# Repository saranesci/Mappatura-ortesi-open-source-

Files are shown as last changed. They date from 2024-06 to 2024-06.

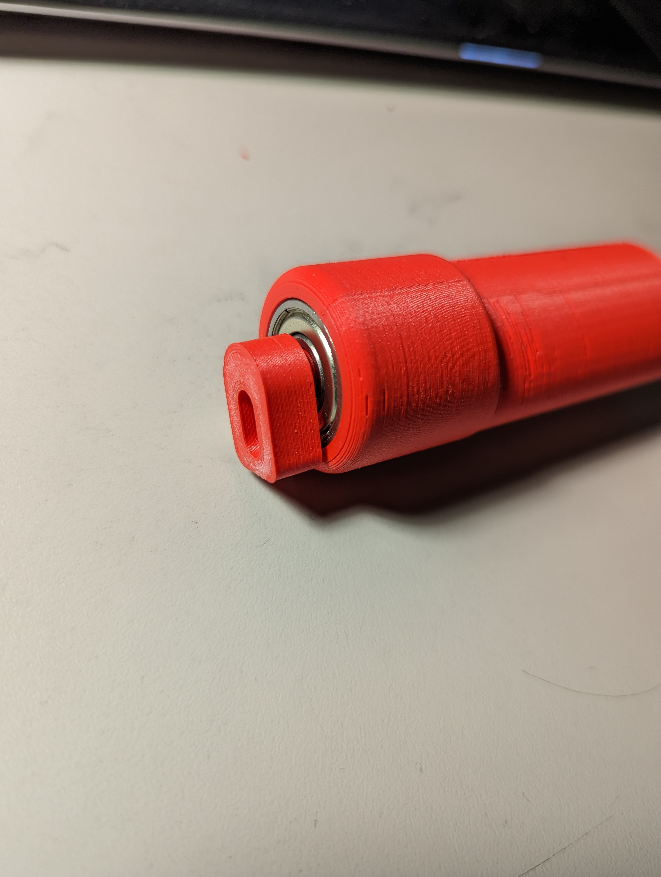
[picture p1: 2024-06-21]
Spoon stabilizer support/spoon-stabilizer-support-main/Photos/handle assembly.jpg

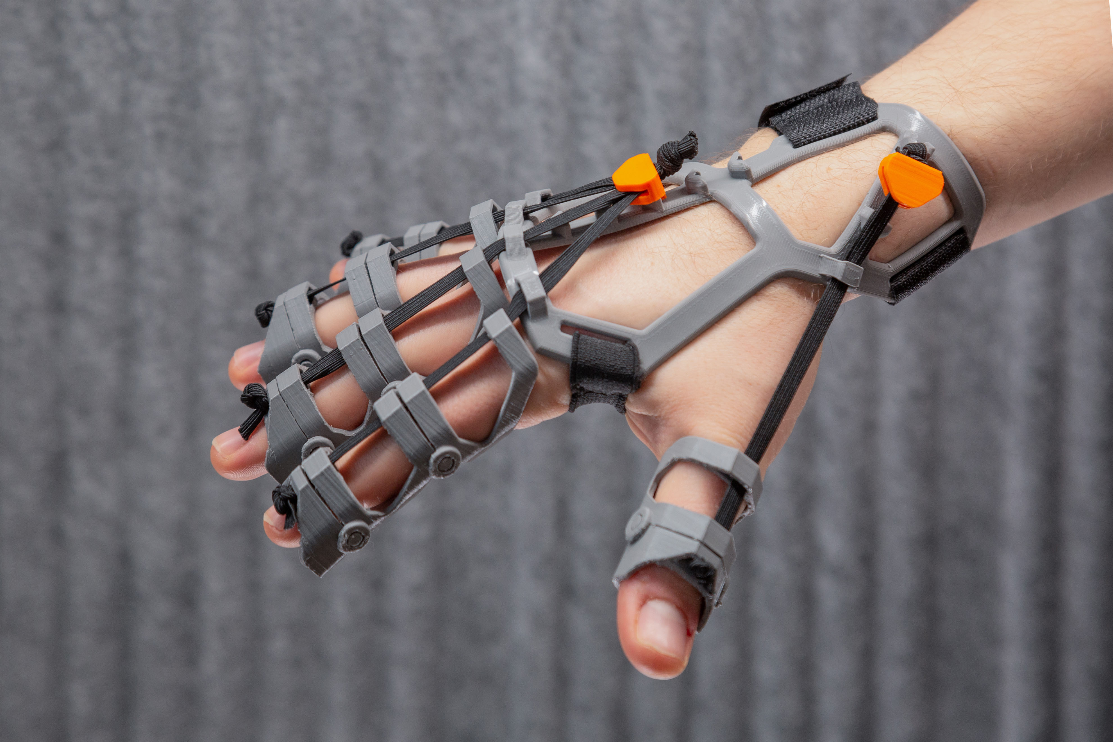
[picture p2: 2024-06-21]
Improving fine motor skills, designing a 3D FDM printed orthosis to assist in the rehabilitation of individuals with hand spasticity/images/9a8a8b08-8b19-4f01-8956-d06154abd471.jpg

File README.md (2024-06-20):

# Mappatura-ortesi-open-source-
Questo repository è una raccolta di soluzioni open source progettate per supportare i lavoratori con disabilità e aiutarli a svolgere le loro mansioni in modo sicuro ed efficiente. L'obiettivo è promuovere l'inclusione lavorativa fornendo un accesso gratuito e aperto a soluzioni assistive innovative.

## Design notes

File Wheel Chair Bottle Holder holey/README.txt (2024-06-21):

Wheel Chair Bottle Holder holey by Diselico on Thingiverse: https://www.thingiverse.com/thing:3944166

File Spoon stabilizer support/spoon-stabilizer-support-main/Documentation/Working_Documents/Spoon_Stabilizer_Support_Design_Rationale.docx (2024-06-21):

# Introduction

A device for those who have difficulties with tremors when eating. It used both passive stabilization and weights to dampen the effect of hand tremors.

# Research

Below is a table of existing commercial or DIY options that are similar.

Name | Picture | Price | Link

Commercial

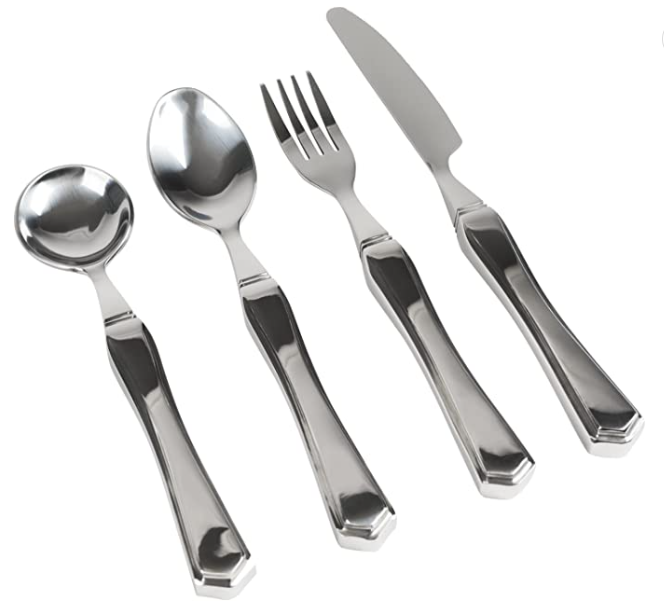
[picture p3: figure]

Vive Weighted Utensils | | $55.46 | Link (https://www.amazon.ca/Vive-7oz-Weighted-Utensils-Piece/dp/B075Y3N1MZ)

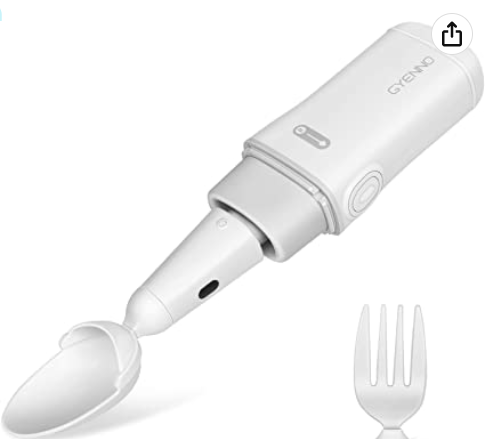
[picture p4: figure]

GYENNO Bravo Twist | | $399 | Link (https://www.amazon.ca/GYENNO-Twist-Parkinson-Stabilizing-Parkinsons/dp/B07FRPX2H8?hvadid=353068188462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)

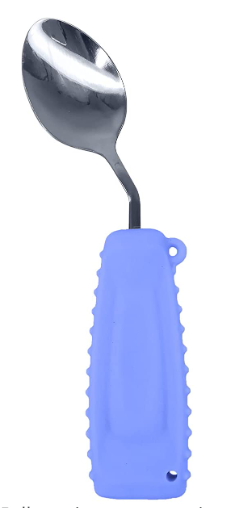
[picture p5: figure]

Ehucon Adaptive Utensils | | $22.32 | Link (https://www.amazon.ca/Ehucon-Untensils-Parkinsons-Lightweight-Ergonomic/dp/B09QGBSPK9?hvadid=353068188462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)

DIY

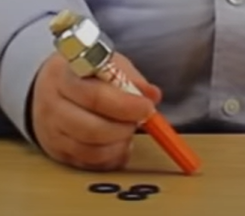
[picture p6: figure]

DIY Weighted Marker | | N/A | Link (https://www.youtube.com/watch?v=PVcX0uTqMMg)

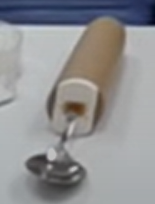
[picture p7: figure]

DIY Weighted Fork | | N/A | Link (https://ohanaot.com/make-weighted-pencil-fork-spoon-kids-autism/)

# Requirements

## Goals

G01 | Create a weighted utensil that stabilizes the tremors of a user’s hand

## Functional Requirements

F01 | Device must be weighted
F02 | Device must have passive spill prevention
F03 | Device must be cleanable

## Non-functional Requirement

NF01 | Device must be made from off the shelf components and 3D printed parts

## Constraints

C01 | Device must cost less than 10 dollars

# Testing

After assembling the device, it was tested to see if it would fail. It was found that 20% infill was too weak for some parts, so they were changed to 100% infill for added strength.

# Opportunities for Improvement

The device could be printed in ABS or another dishwasher safe material.

Printability improvements could be made to reduce support use.

© 2023 by Neil Squire. This work is licensed under the CC BY SA 4.0 License: http://creativecommons.org/licenses/by-sa/4.0 Files available at https://makersmakingchange.com/project/spoon-stabilizer-support/ Page 2 of 3

V1.0 | February 2023 Spoon Stabilizer Support Design Rationale

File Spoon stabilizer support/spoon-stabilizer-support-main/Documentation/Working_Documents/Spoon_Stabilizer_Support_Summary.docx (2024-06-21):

# Title

Spoon Stabilizer Support

## Subtitle

A device for those who have difficulties with tremors when eating. The Spoon Stabilizer Support uses both passive stabilization and weights to dampen the effect of hand tremors.

## Device Details

### Overview

A device for those who have difficulties with tremors when eating. It used both passive stabilization and weights to dampen the effect of hand tremors.

### Usage

Attach either the spoon or fork attachment to the handle using the set screw. The device can then be used as a normal spoon or fork.

### Cost

<$5

### Build Instructions

After all supports are removed, superglue the bearing into the handle, and the insert into the bearing. Cut the spoon near the head, and glue it into the spoon attachment. Connect the spoon attachment to the insert using the computer case screws. If the user wants a weighted handle, insert the fishing weights into the handle. Finally, glue the grip insert onto the end of the handle.

#### Skills Required

- 3D Printing

#### Time Required

3D Printing Time: 308 min

Assembly Time: 10 min

#### Tools

- 3D Printer
- Tin Snips
- Superglue
- Hot Glue

#### Components

- Bearings
- Computer Case Screws
- Fishing Weights
- Utensil

#### 3D Printing

- Grip Handle
- Grip Insert
- Insert
- Spoon attachment

### Attribution

Design by Ian Faulkner (https://www.printables.com/social/380579-ian-faulkner/about)

Documentation by Neil Squire Society/Makers Making Change

© 2023 by Neil Squire. This work is licensed under the CC BY SA 4.0 License: http://creativecommons.org/licenses/by-sa/4.0 Files available at https://makersmakingchange.com/project/spoon-stabilizer-support/ Page 2 of 3

V1.0 | February 2023 Spoon Stabilizer Support Summary

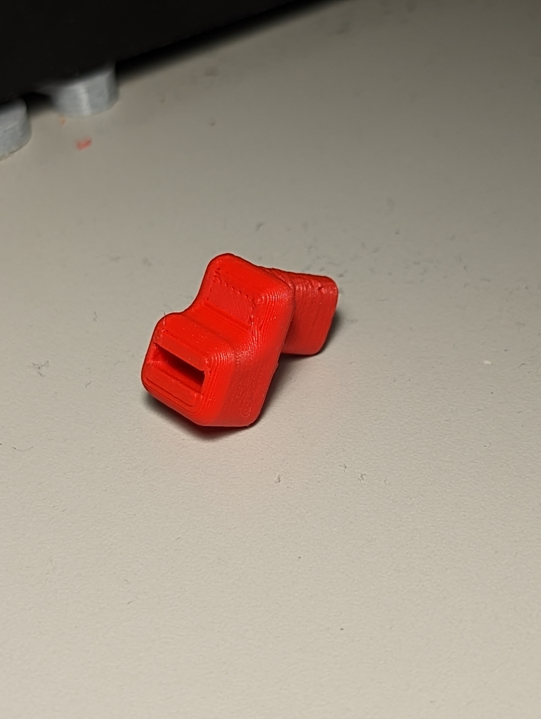
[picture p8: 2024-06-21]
Spoon stabilizer support/spoon-stabilizer-support-main/Photos/spoon attachment.jpg

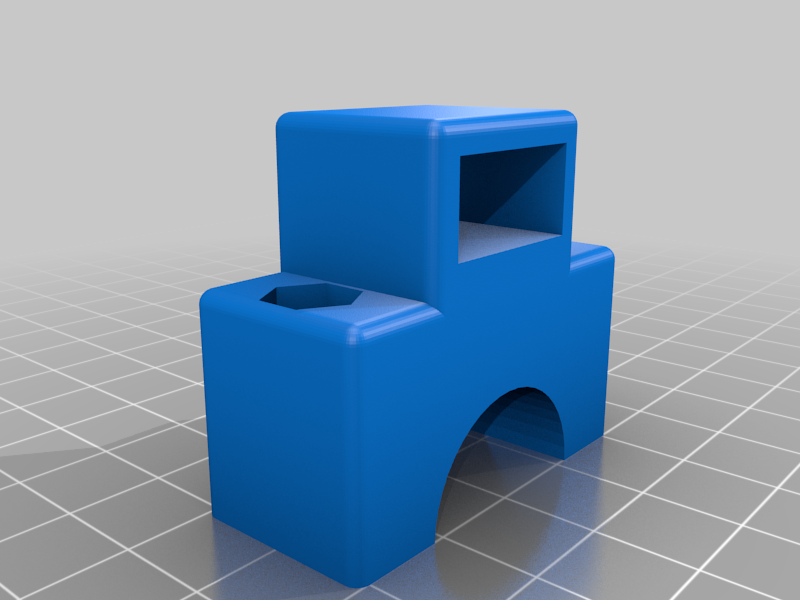
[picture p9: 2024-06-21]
Wheel Chair Bottle Holder holey/images/4a7bebc6-be08-4650-9d3e-f749b71c4481.png

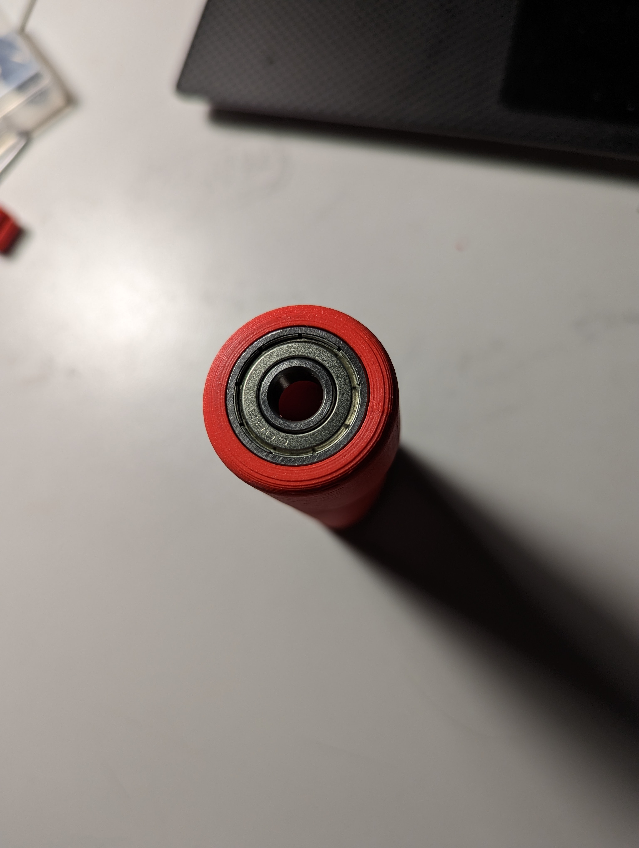
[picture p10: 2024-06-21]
Spoon stabilizer support/spoon-stabilizer-support-main/Photos/bearing inserted.jpg

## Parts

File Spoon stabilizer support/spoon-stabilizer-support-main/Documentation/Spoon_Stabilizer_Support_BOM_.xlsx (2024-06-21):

Device: Spoon Stabilizer Support |  | Total Cost | Total Print time (hr) | Total filament (g)
Version: V1.0 | Date Created: 2/14/2023 | $6.95 | 4.97 | 33
Commercial Parts:
Part type (Electrical. Mechanical, Sanitization, ect) | Part Name | Quantity Needed | Pkg Quantity | Price per package | Price per Unit | Price for qty needed | Link
Mechanical | Bearings | 1 | 10 | $11.55 | $1.16 | $1.16 | https://www.amazon.ca/gp/product/B07XLV1W2M/ref=ppx_yo_dt_b_asin_title_o00_s00?ie=UTF8&psc=1
Mechanical | Computer Case Screws | 1 | 10 | $9.89 | $0.99 | $0.99 | https://www.amazon.ca/gp/product/B07TXS98L6/ref=ppx_yo_dt_b_asin_title_o00_s00?ie=UTF8&psc=1
Mechanical | Fishing Weights | 2 | 10 | $13.99 | $1.40 | $2.80 | https://www.amazon.ca/gp/product/B0B1JBJ91F/ref=ppx_yo_dt_b_asin_title_o00_s00?ie=UTF8&psc=1
Mechanical | Spoon | 1 | 12 | $14.17 | $1.18 | $1.18 | https://www.amazon.ca/Winco-0005-03-12-Piece-Dinner-Stainless/dp/B004UNF2II
3D Printed Parts ESTIMATED PRICING USING 1KG ROLL COST: | $25.00
Part | Description | Quantity Needed | TOTAL Mass (g) | Estimated Price | Print Time (Min) | Link
Grip Handle | Main Handle | 1 | 26 | $0.65 | 224
Grip Insert | Handle endcap | 1 | 2 | $0.05 | 15
insert | Connects spoon to bearing | 1 | 2 | $0.05 | 27
spoon attachment | Connects to spoon | 1 | 3 | $0.07 | 32
 |  |  |  | $0.00
 |  |  | Total Print Cost: | $0.83
Tools for Assembly
Alternatives (if there are other sources for some parts link them below)
Part and description | Link

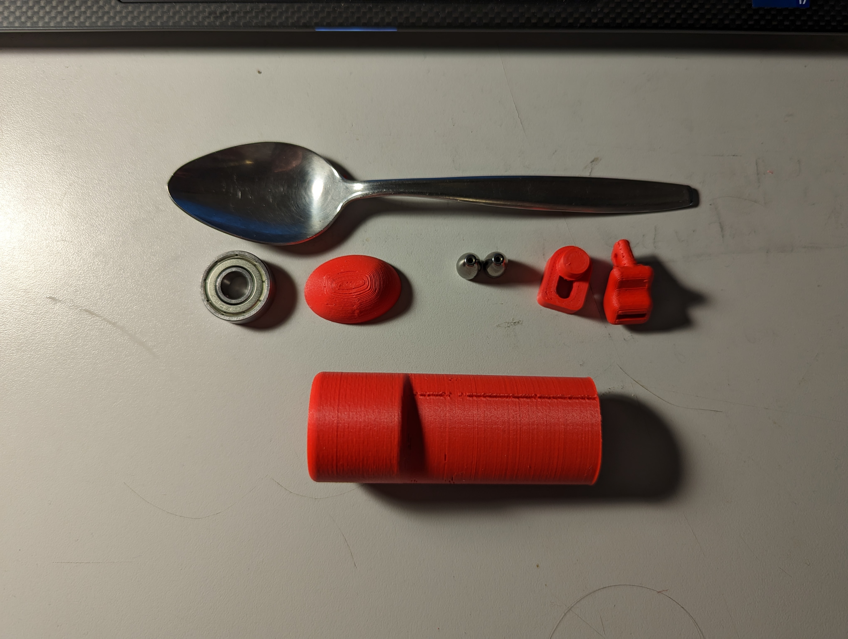
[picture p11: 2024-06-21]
Spoon stabilizer support/spoon-stabilizer-support-main/Photos/Parts layout.jpg

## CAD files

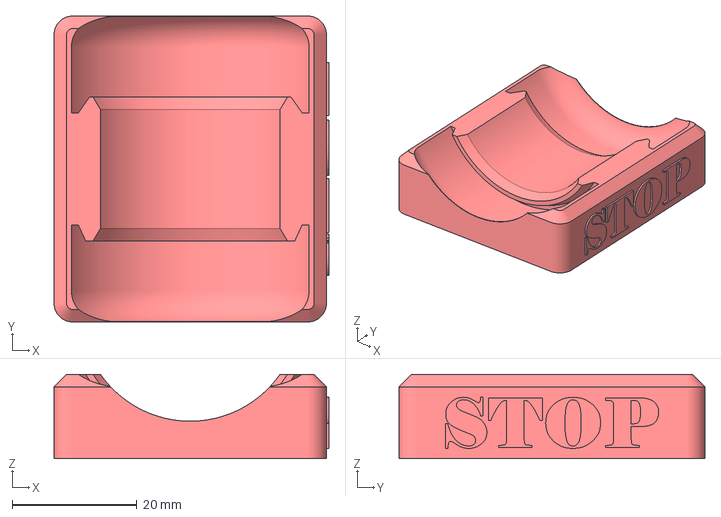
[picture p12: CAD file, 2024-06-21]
Chair stop wheel holder/Chair Stop, Wheel holder.3mf
44.0 x 49.0 x 13.5 mm

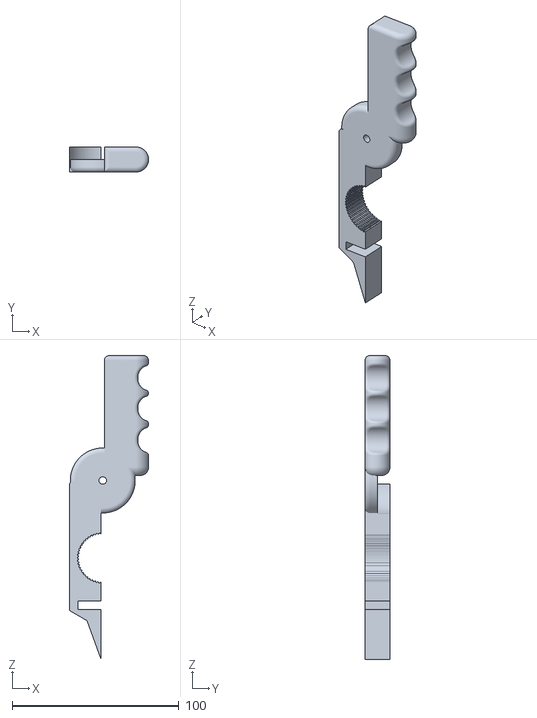
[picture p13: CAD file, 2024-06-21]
Gripsy - Tool for disabled people/files/gripsy_left.stl
47.5 x 15.0 x 182.4

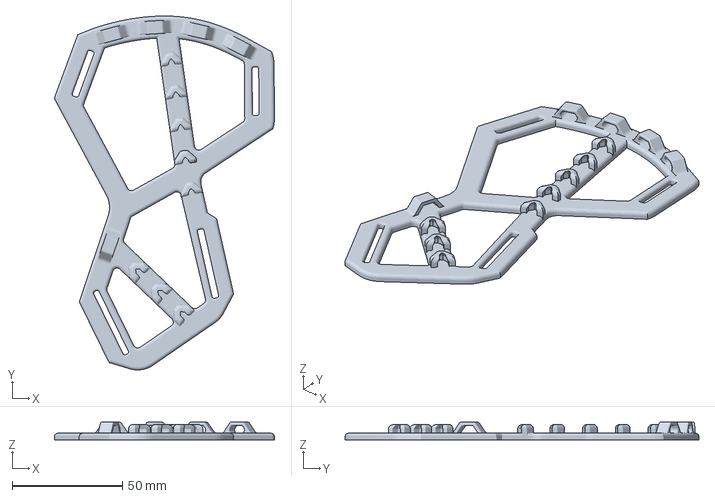
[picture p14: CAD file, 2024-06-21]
Improving fine motor skills, designing a 3D FDM printed orthosis to assist in the rehabilitation of individuals with hand spasticity/files/hand_heated_part.3mf
99.8 x 160.6 x 8.00 mm

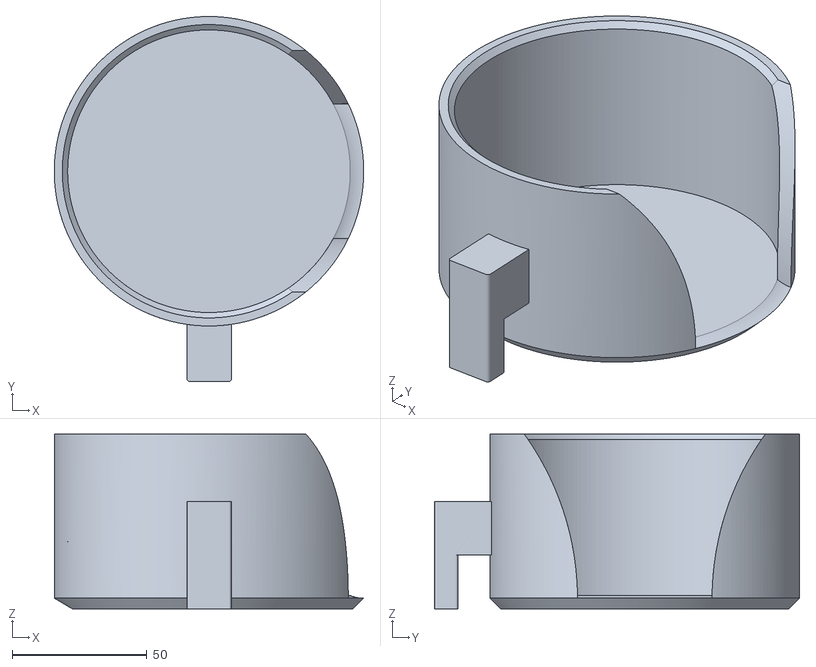
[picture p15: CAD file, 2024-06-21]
NewSkill wheelchair cup holder/files/cup_right.stl
115.0 x 135.6 x 65.0

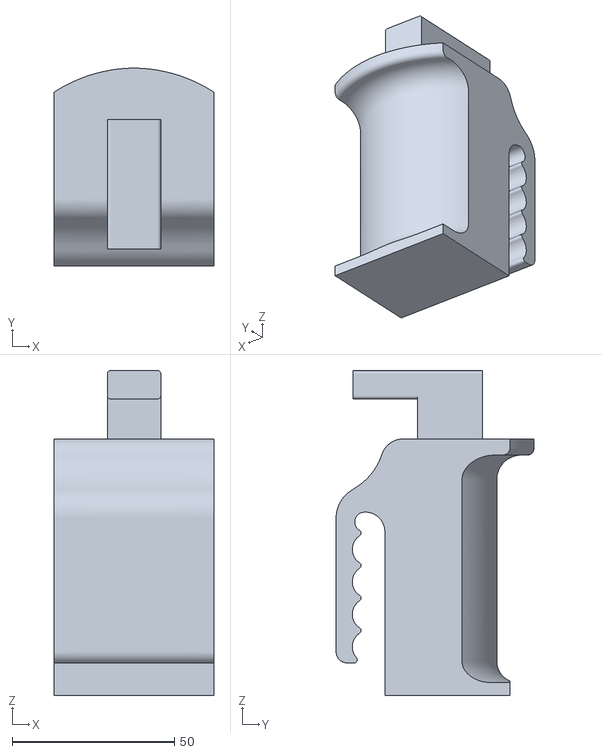
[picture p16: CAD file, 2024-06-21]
NewSkill wheelchair cup holder/NewSkill wheelchair headphones holder - 6606261/files/Headphones_Holder.stl
49.2 x 60.9 x 100.1

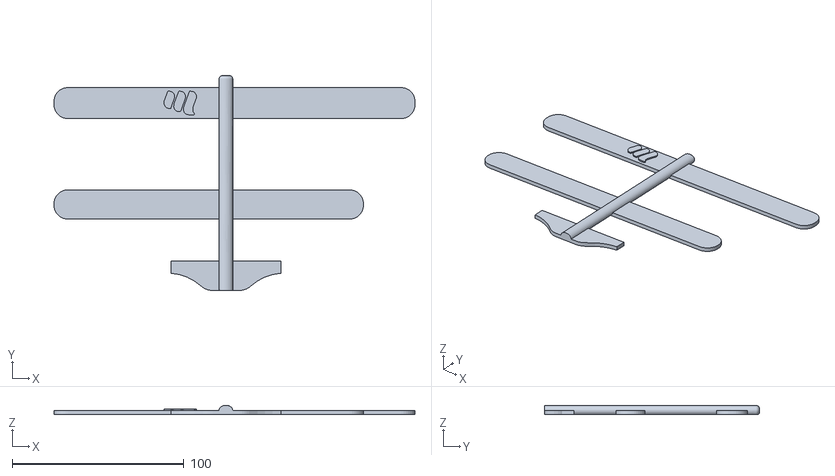
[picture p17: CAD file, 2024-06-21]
Orthosis for Typing and touchscreen/files/Typing_orthosis.STL
210.0 x 125.0 x 5.50

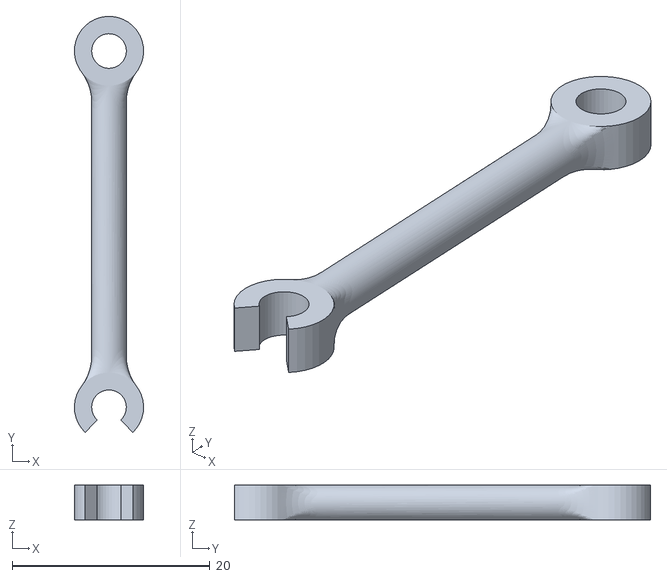
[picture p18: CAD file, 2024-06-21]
Printed Rehabilitation Orthosis/3D Printed Orthosis Free Source Files and Assembly Guide/Finger 1/1d.STL
7.00 x 42.0 x 3.50

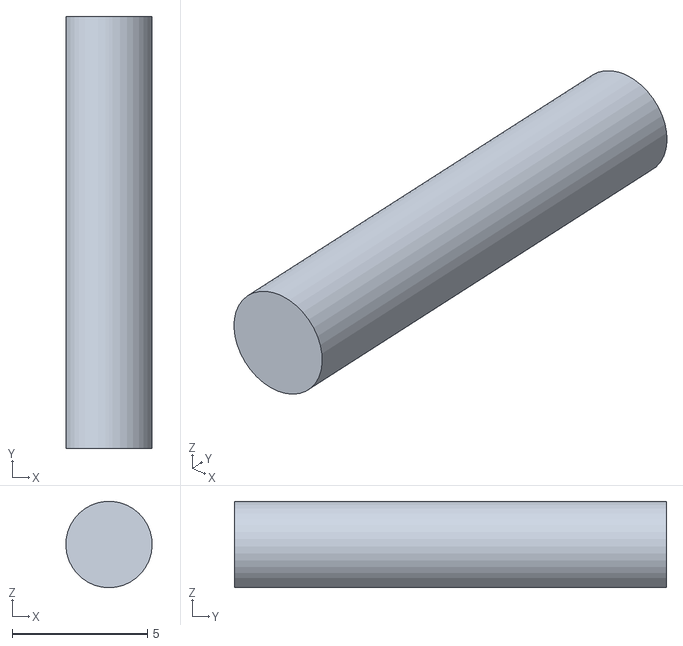
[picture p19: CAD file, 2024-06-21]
Printed Rehabilitation Orthosis/3D Printed Orthosis Free Source Files and Assembly Guide/Finger 2/2k.STL
3.20 x 16.0 x 3.20

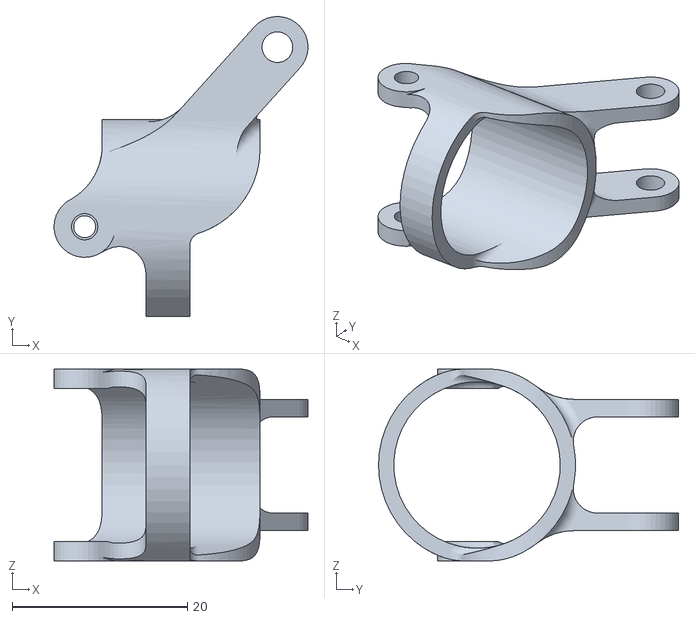
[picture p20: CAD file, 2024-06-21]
Printed Rehabilitation Orthosis/3D Printed Orthosis Free Source Files and Assembly Guide/Finger 3/3c.STL
29.0 x 34.2 x 21.9

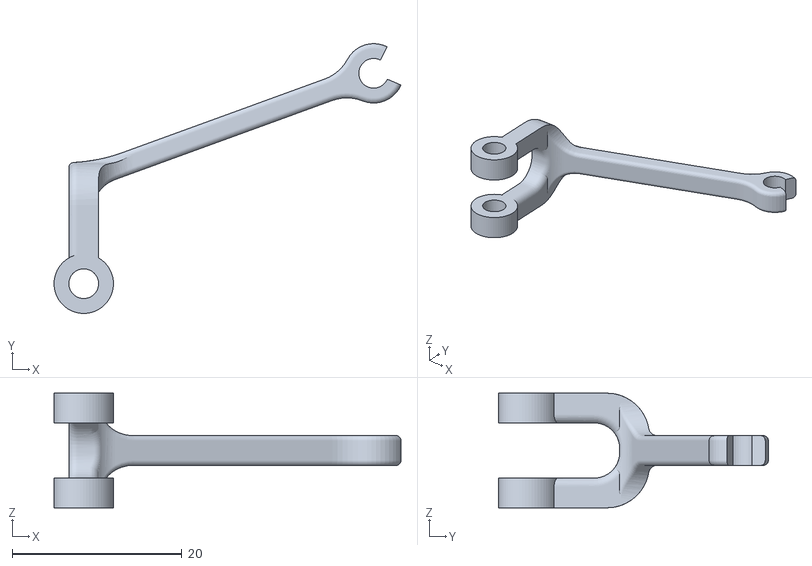
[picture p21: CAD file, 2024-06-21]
Printed Rehabilitation Orthosis/3D Printed Orthosis Free Source Files and Assembly Guide/Finger 4/4f.STL
40.8 x 31.8 x 13.5

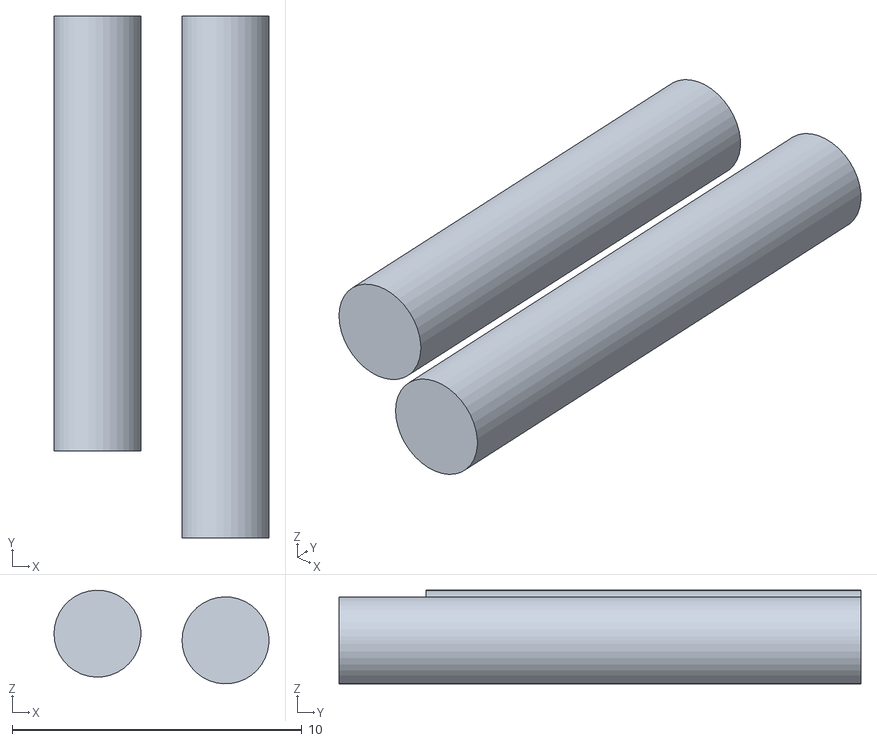
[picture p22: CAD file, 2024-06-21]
Printed Rehabilitation Orthosis/3D Printed Orthosis Free Source Files and Assembly Guide/Finger 5/5h.STL
7.42 x 18.0 x 3.23

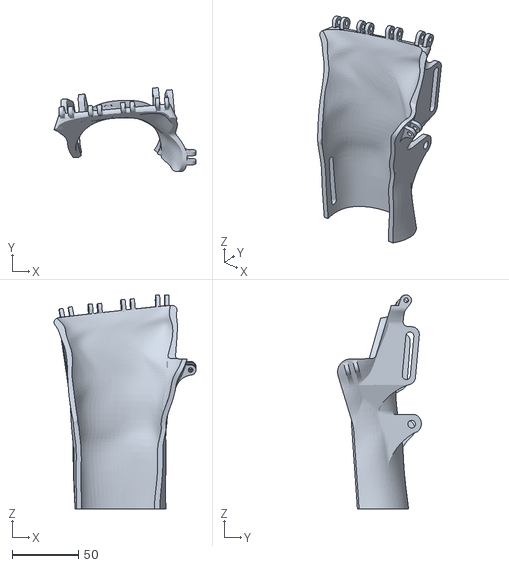
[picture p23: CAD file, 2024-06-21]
Printed Rehabilitation Orthosis/3D Printed Orthosis Free Source Files and Assembly Guide/Husk/0.STL
107.1 x 63.3 x 161.5

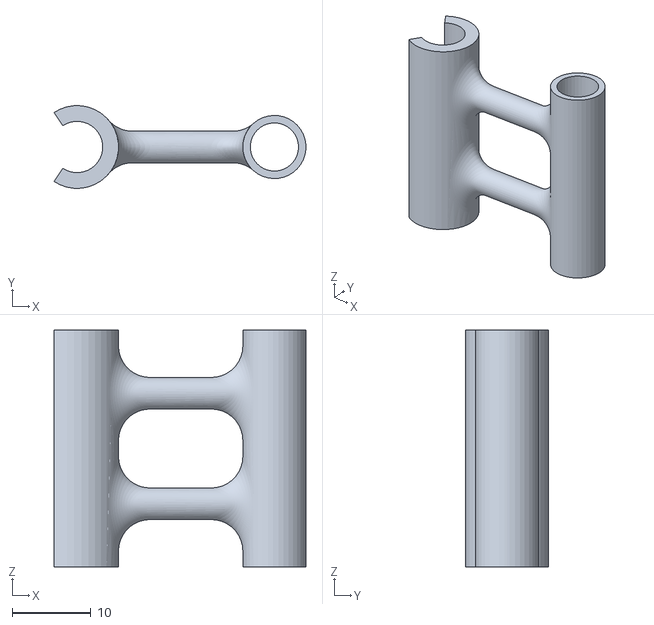
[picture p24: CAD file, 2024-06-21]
Printed Rehabilitation Orthosis/3D Printed Orthosis Free Source Files and Assembly Guide/Lever mechanism and pin/6c.STL
31.9 x 10.5 x 30.0

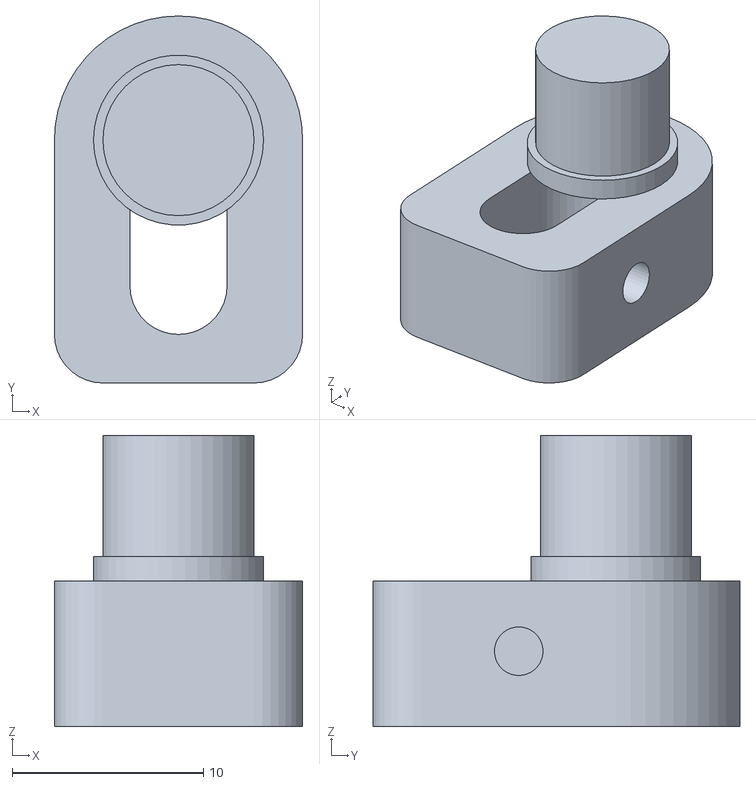
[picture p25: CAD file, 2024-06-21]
Spoon stabilizer support/spoon-stabilizer-support-main/Build_Files/3D_Printing_Files/insert.STL
13.0 x 19.2 x 15.2

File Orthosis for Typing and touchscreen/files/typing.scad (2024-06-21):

/* [Parameters] */
tip_perimeter=64;
tip_width=17;

mid_perimeter=200;
mid_width=17;

bottom_perimeter=210;
bottom_width=17;

distance_tip_mid=24.5;
distance_mid_bottom=41.5;

thickness=2.5;

/* [Hidden] */
e=thickness;
r=8;
r2=2;
tfp=tip_perimeter;
tfw=tip_width;

mp=mid_perimeter;
mw=mid_width;

bp=bottom_perimeter;
bw=bottom_width;

dtm=distance_tip_mid;
dmb=distance_mid_bottom;

//modulos
module cubox(l1,w1,e1,r1){
hull(){
translate([l1/2-r1,w1/2-r1,0]){
cylinder(e1,r1,r1,$fn=100, center=true);
}
translate([l1/2-r1,-w1/2+r1,0]){
cylinder(e1,r1,r1,$fn=100, center=true);
}
translate([-l1/2+r1,-w1/2+r1,0]){
cylinder(e1,r1,r1,$fn=100, center=true);
}
translate([-l1/2+r1,w1/2-r1,0]){
cylinder(e1,r1,r1,$fn=100, center=true);

}
}
}


//TIP
cube(size=[tfp,tfw*0.4,e] , center=true);

difference() {
translate([0,tfw*0.5-r2/2,0]){
union(){
cube(size=[tfp*0.375+2*tfw*0.6,tfw*0.6-r2,e] , center=true);
translate([0,r2/2,0]){
cubox(tfp*0.375,tfw*0.6,e  ,r2);
}
}
}
    union() {
    translate([-(tfp*0.375/2+tfw*0.6),tfw*0.8,0]){
    cylinder(e+2,tfw*0.6,tfw*0.6, center=true);
    }
   translate([tfp*0.375/2+tfw*0.6,tfw*0.8,0]){
    cylinder(e+2,tfw*0.6,tfw*0.6, center=true);
    } 
    }

}

//MIDDLE
dtm2=dtm+0.4*tfw/2+mw/2;
translate([0,-dtm2,0]){  
cubox(mp,mw,e,r);
}

//BOTTOM
dmb2=dmb+bw/2+mw/2;
translate([0,-dtm2-dmb2,0]){  
cubox(bp,bw,e,r);
}

//union
cl=tfw+dtm+mw+dmb+bw;
translate([0,-cl/2+tfw*0.8,0]){
difference() { 
rotate([90,0,0]){ 
scale([1.3,1,1]){
cylinder(cl,3,3, center=true);
}
}
translate([0,0,-(10+e)/2]){ 
cube(size=[10,cl+10,10] , center=true);
}
}
}

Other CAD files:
Spoon stabilizer support/spoon-stabilizer-support-main/Design_Files/CAD_Design_Files/insert.step
Utensil Holder/files/Utensil_holder_right.stl
Wheel Chair Bottle Holder holey/files/Pince-01b.STL
Gripsy - Tool for disabled people/files/gripsy_right.stl
Gripsy - Tool for disabled people/files/schaar3deel3.stl
Improving fine motor skills, designing a 3D FDM printed orthosis to assist in the rehabilitation of individuals with hand spasticity/files/finger.3mf
Improving fine motor skills, designing a 3D FDM printed orthosis to assist in the rehabilitation of individuals with hand spasticity/files/strap.3mf
Improving fine motor skills, designing a 3D FDM printed orthosis to assist in the rehabilitation of individuals with hand spasticity/files/thumb.3mf
NewSkill wheelchair cup holder/files/cup_left.stl
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

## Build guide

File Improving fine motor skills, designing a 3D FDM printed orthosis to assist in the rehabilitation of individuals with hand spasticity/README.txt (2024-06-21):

Improving fine motor skills, designing a 3D FDM printed orthosis to assist in the rehabilitation of individuals with hand spasticity by Piotrownik on Thingiverse: https://www.thingiverse.com/thing:6610431

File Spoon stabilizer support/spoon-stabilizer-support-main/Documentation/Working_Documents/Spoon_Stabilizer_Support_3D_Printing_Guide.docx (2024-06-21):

# 3D Printing Summary

Metrics
Total Print Time (min) | 308
Total Number of Components | 4
Typical Total Mass (g) | 33
Typical Number of Print Setups | 4

# 3D Printing Settings

Print File Name | Qty | Total Print Time (hr:min) | Mass (g) | Infill (%) | Support(Y/N) | Layer Height/ Nozzle Diameter(mm) | Notes (orientation, special settings, etc.)
Grip Handle.stl | 1 | 3:44 | 26 | 20 | Y | 0.2/0.4 | - Requires support - Print in orientation given in STL
Grip Insert.stl | 1 | 0:15 | 2 | 20 | N | 0.2/0.4 | - Print in orientation given in STL
insert.stl | 1 | 0:27 | 2 | 20 | Y | 0.2/0.4 | - Requires support - Print in orientation given in STL
spoon attachment.stl | 1 | 0:32 | 3 | 20 | Y | 0.2/0.4 | - Requires support - Print in orientation given in STL

# Customization Options

- The device can be printed in any colour the user would like.

# Post-Processing

- Remove support material
- Remove any sharp edges using a hobby knife or sandpaper

# Examples of Quality Prints

Photos of Grip Handle.stl

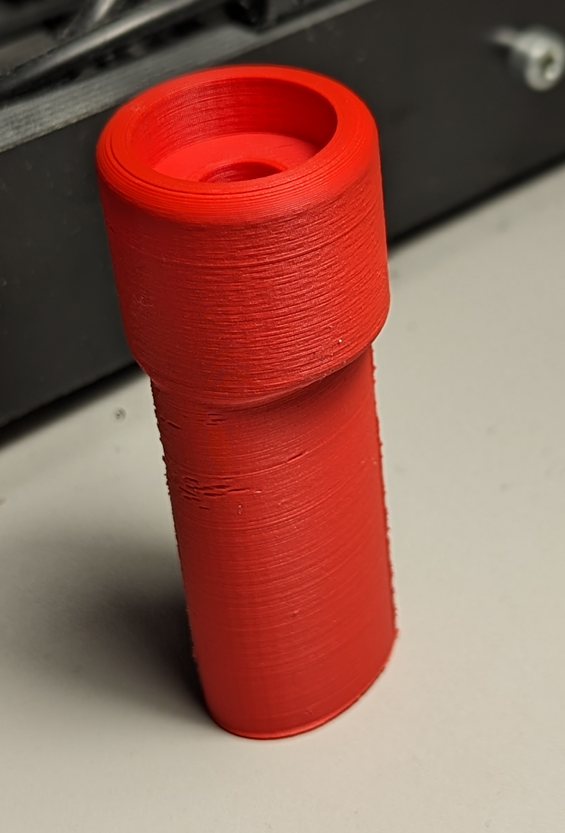
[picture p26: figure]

Photos of Grip Insert.stl

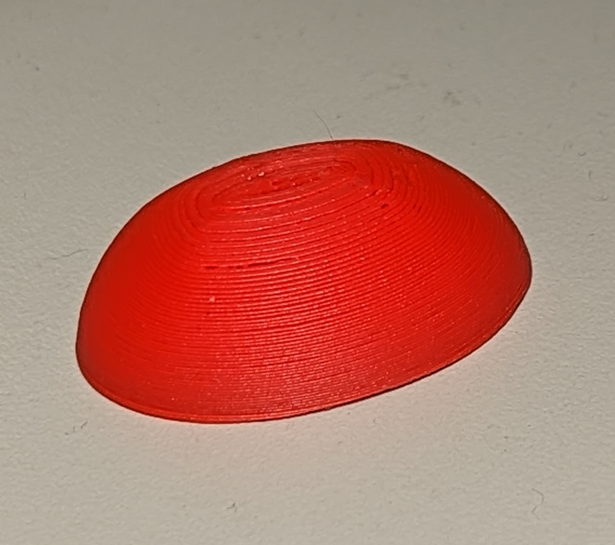
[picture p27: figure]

Photos of insert.stl

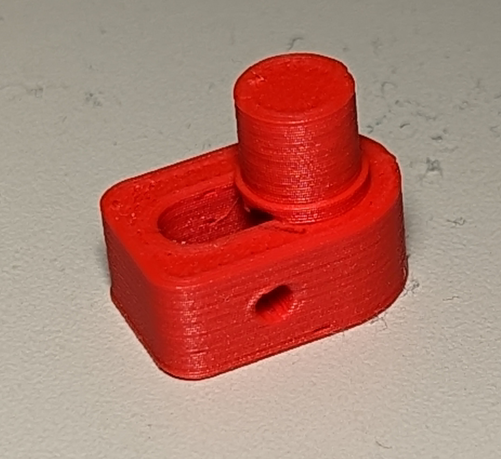
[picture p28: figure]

Photos of spoon attachment.stl

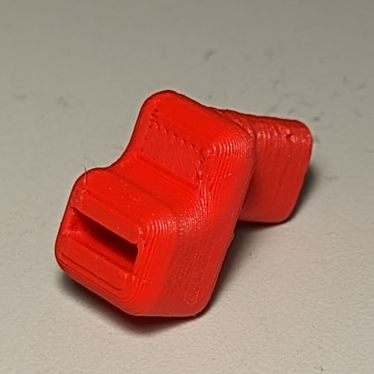
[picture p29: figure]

© 2023 by Neil Squire. This work is licensed under the CC BY SA 4.0 License: http://creativecommons.org/licenses/by-sa/4.0 Files available at https://makersmakingchange.com/project/spoon-stabilizer-support/ Page 1 of 2

V1.0 | February 2023 Spoon Stabilizer Support 3D Printing Guide

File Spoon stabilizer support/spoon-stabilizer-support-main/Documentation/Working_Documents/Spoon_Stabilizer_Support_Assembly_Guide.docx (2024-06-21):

# Required Components

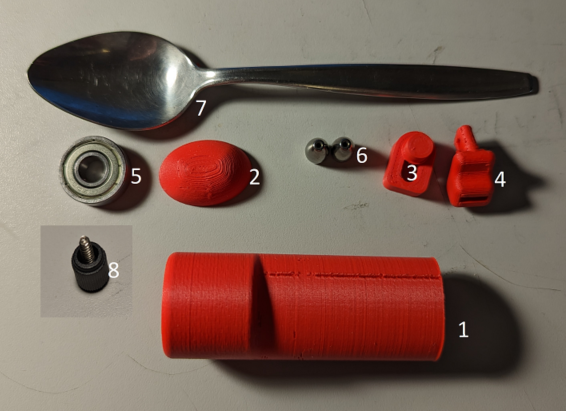
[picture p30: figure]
All components of the device, laid out and numbered.

| BOM 1. Grip Handle 2. Grip insert 3. Insert 4. Spoon attachment 5. Bearing 6. Fishing weights 7. Utensil 8. Computer case screw

# Required Tools

- Tin Snips
- Superglue
- Hot Glue

# Required Personal Protective Equipment (PPE)

- Eye protection

# Assembly Instructions

## Step 1

Use superglue to glue the bearing into the grip handle. Be careful to not get any into the bearing.

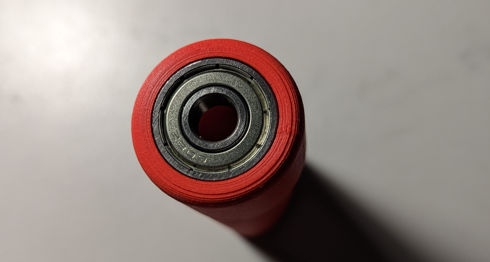
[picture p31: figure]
The handle of the device with the bearing glued in place.

## Step 2

Use superglue to attach the insert into the bearing. Be careful not to get any into the bearing.

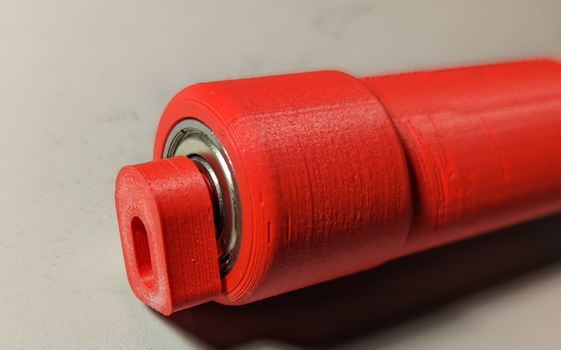
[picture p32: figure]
The handle and bearing with the insert glued into the centre of the bearing.

## Step 3

Cut the utensil at the desired length and hot glue it into the slot on the spoon attachment.

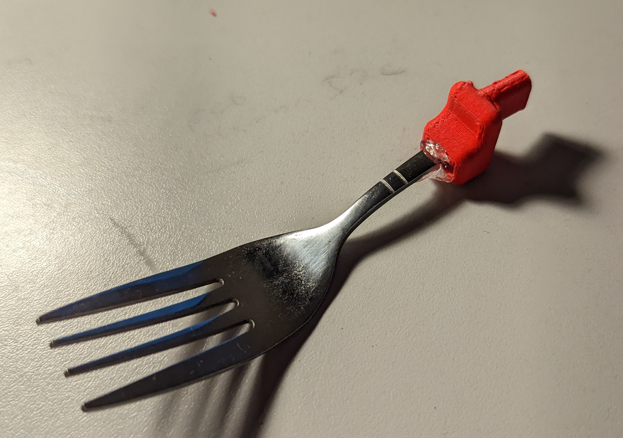
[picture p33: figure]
The utensil attachment with a fork cut to length and glued in place.

## Step 4

Using the set screw, attach the spoon section to the handle section.

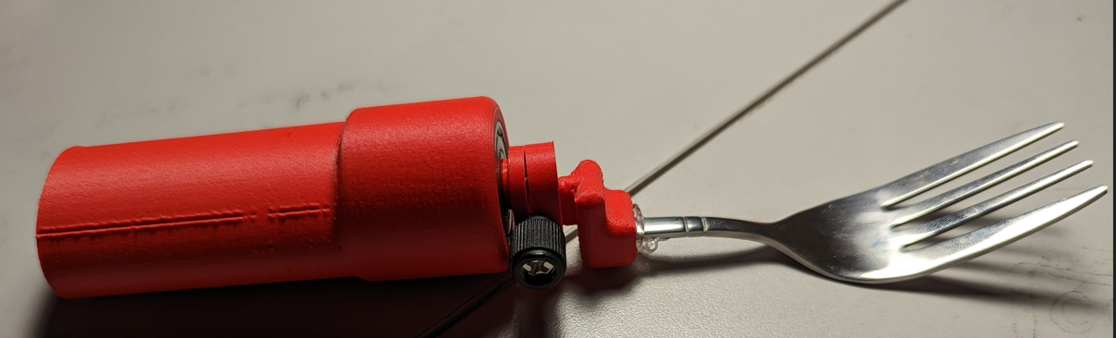
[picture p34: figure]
The utensil attachment attached to the handle assembly.

## Step 5

If the user wants a weighted utensil, add the desired amount of weights to the hollow handle section. A tissue can optionally be used to prevent the weights from sliding around in the handle.

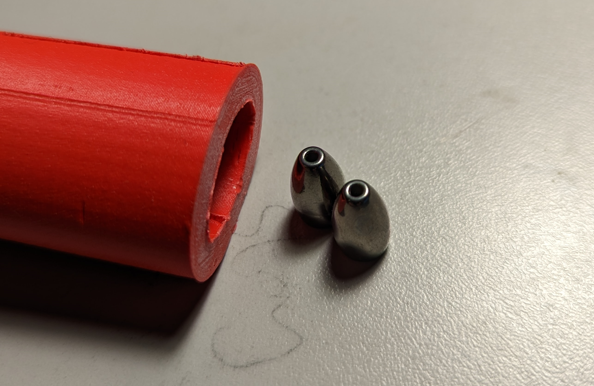
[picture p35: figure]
Two weights next to the hollow device handle.

## Step 6

Use superglue to attach the grip insert to the end of the handle. Optionally, a soldering iron can be used to melt the two pieces together.

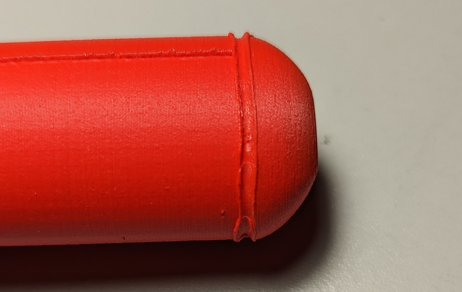
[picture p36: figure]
The handle with the endcap attached.

© 2023 by Neil Squire. This work is licensed under the CC BY SA 4.0 License: http://creativecommons.org/licenses/by-sa/4.0 Files available at https://makersmakingchange.com/project/spoon-stabilizer-support/ Page 2 of 3

V1.0 | February 2023 Spoon Stabilizer Support Assembly Guide

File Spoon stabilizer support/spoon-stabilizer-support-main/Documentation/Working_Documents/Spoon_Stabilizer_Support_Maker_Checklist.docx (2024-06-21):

# Maker To Do List

- Read through the Assembly Guide to become familiar with required components, tools, supplies, and safety gear and overall assembly steps.
- Talk to User about customization options (e.g., color, any special requests, etc.)
- Order hardware components
- Gather tools, supplies, and safety equipment.
- Assemble the device
- Test device
- Print “User Quick Guide”

# Items to Give to User

- Assembled, tested device
- “User Quick Guide”

© 2023 by Neil Squire. This work is licensed under the CC BY SA 4.0 License: http://creativecommons.org/licenses/by-sa/4.0 Files available at https://makersmakingchange.com/project/spoon-stabilizer-support/ Page 2 of 3

V1.0 | February 2023 Spoon Stabilizer Support Maker Checklist

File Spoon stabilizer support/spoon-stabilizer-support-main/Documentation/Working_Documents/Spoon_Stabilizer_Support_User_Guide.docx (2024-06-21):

## Introduction

A device for those who have difficulties with tremors when eating. It uses both passive stabilization and weights to dampen the effect of hand tremors.

## Features

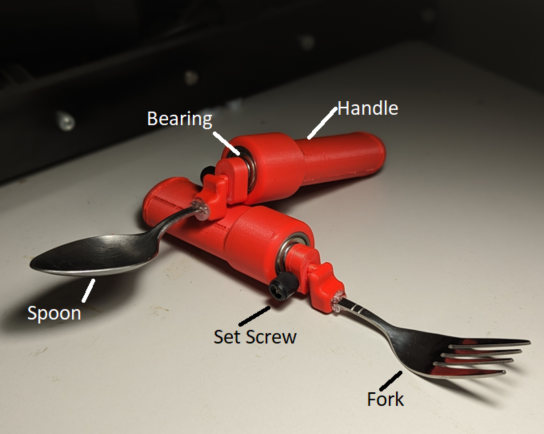
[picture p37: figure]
Labeled picture of two of the devices, one a spoon, and the other a fork

## Usage

Attach either the spoon or fork attachment to the handle using the set screw. The device can then be used as a normal spoon or fork.

## Compatibility

The device is compatible with any spoon or fork that has a cross section of 9x2.5mm or less.

## Specifications

Handle has a length of 90mm, and a diameter of 30mm. The entire device has a weight of 60 g.

## Cleaning

The device can be wiped clean with a damp cloth. The section with the fork/spoon can be detached for easier cleaning.

© 2023 by Neil Squire. This work is licensed under the CC BY SA 4.0 License: http://creativecommons.org/licenses/by-sa/4.0 Files available at https://makersmakingchange.com/project/spoon-stabilizer-support/ Page 1 of 2

V1.0 | February 2023 Spoon Stabilizer Support user Quick Guide

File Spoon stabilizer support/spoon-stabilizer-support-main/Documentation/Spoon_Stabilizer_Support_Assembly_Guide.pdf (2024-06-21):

V1.0 | February 2023

# Spoon Stabilizer Support

# ASSEMBLY GUIDE

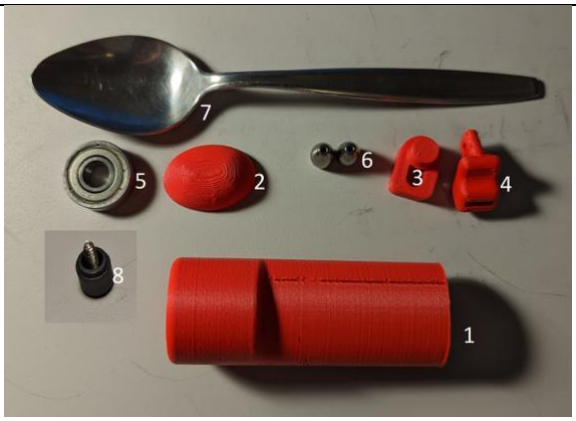
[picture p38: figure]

© 2023 by Neil Squire. (https://neilsquire.ca/)
This work is licensed under the CC BY SA 4.0 License: http://creativecommons.org/licenses/by-sa/4.0
Files available at https://makersmakingchange.com/project/spoon-stabilizer-support/ | Page 1 of 4

# Required Components

## BOM 1. Grip Handle 2. Grip insert 3. Insert 4. Spoon attachment 5. Bearing 6. Fishing weights 7. Utensil 8. Computer case screw

# Required Tools

## - Tin Snips - Superglue - Hot Glue

# Required Personal Protective Equipment (PPE)

## - Eye protection

# ASSEMBLY GUIDE

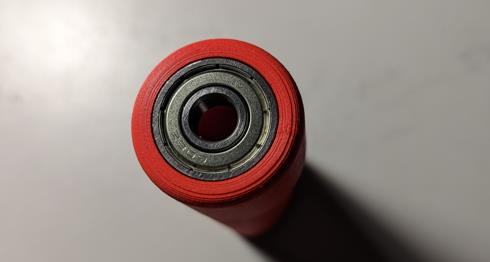
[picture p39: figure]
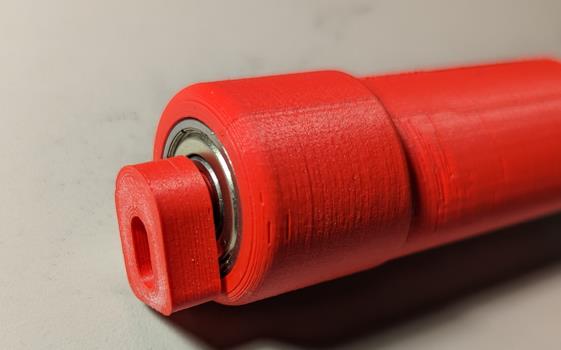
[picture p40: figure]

Files available at https://makersmakingchange.com/project/spoon-stabilizer-support/ | Page 2 of 4

# Assembly Instructions

## Step 1

Use superglue to glue the bearing into the grip handle. Be careful to not get any into the bearing.

## Step 2

Use superglue to attach the insert into the bearing. Be careful not to get any into the bearing.

# ASSEMBLY GUIDE

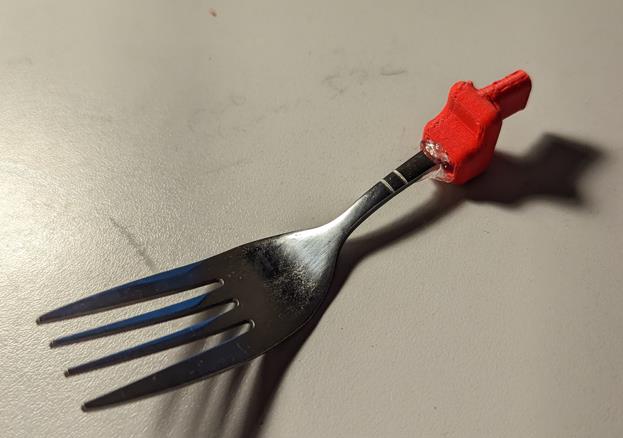
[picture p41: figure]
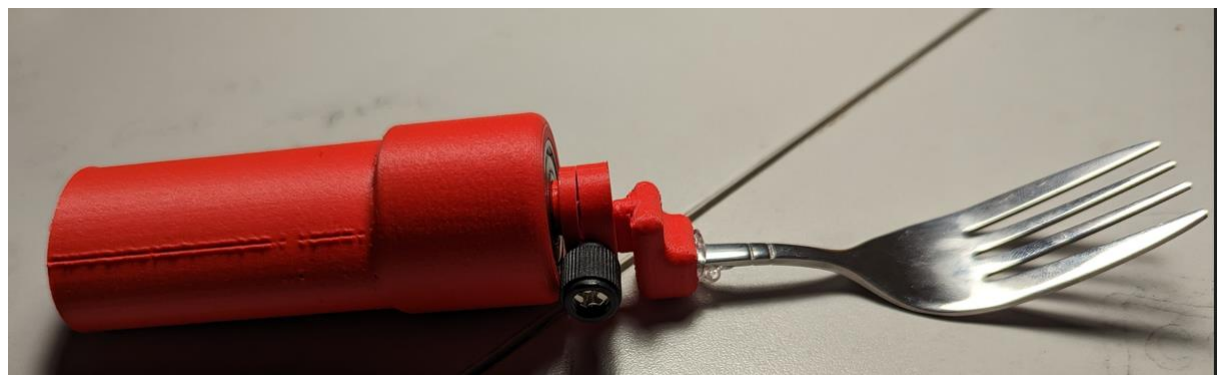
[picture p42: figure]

Files available at https://makersmakingchange.com/project/spoon-stabilizer-support/ | Page 3 of 4

## Step 3

Cut the utensil at the desired length and hot glue it into the slot on the spoon attachment.

## Step 4

Using the set screw, attach the spoon section to the handle section.

# ASSEMBLY GUIDE

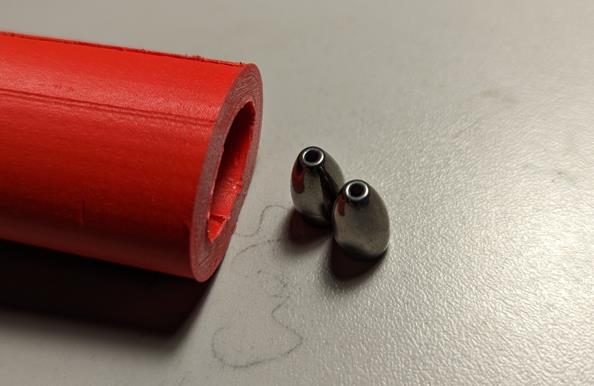
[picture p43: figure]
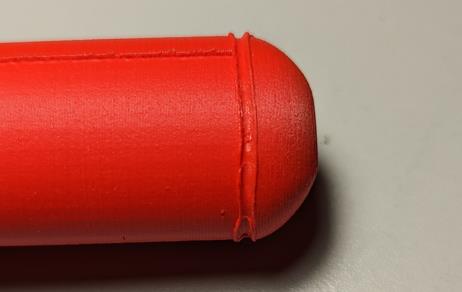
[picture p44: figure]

Files available at https://makersmakingchange.com/project/spoon-stabilizer-support/ | Page 4 of 4

## Step 5

If the user wants a weighted utensil, add the desired amount of weights to the hollow handle section. A tissue can optionally be used to prevent the weights from sliding around in the handle.

## Step 6

Use superglue to attach the grip insert to the end of the handle. Optionally, a soldering iron can be used to melt the two pieces together.

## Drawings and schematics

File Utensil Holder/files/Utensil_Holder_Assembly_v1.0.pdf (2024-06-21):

# Utensil Holder

# ASSEMBLY MANUAL

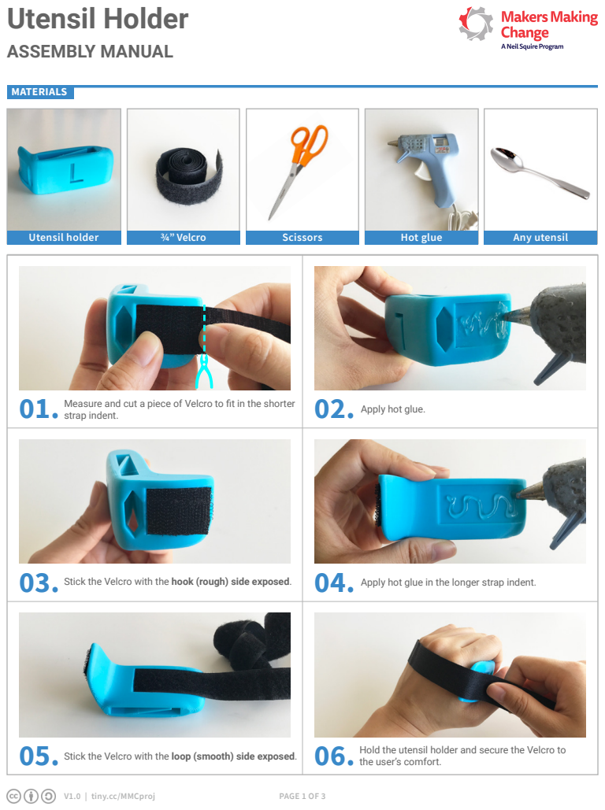
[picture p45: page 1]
V1.0 | tiny.cc/MMCproj; PAGE 1 OF 3; MATERIALS; Utensil holder; ¾” Velcro; Scissors; Hot glue; Any utensil

01. Measure and cut a piece of Velcro to fit in the shorter strap indent. | 02. Apply hot glue.

03. Stick the Velcro with the hook (rough) side exposed. | 04. Apply hot glue in the longer strap indent.

05. Stick the Velcro with the loop (smooth) side exposed. | 06. Hold the utensil holder and secure the Velcro to the user’s comfort.

# Utensil Holder

# ASSEMBLY MANUAL

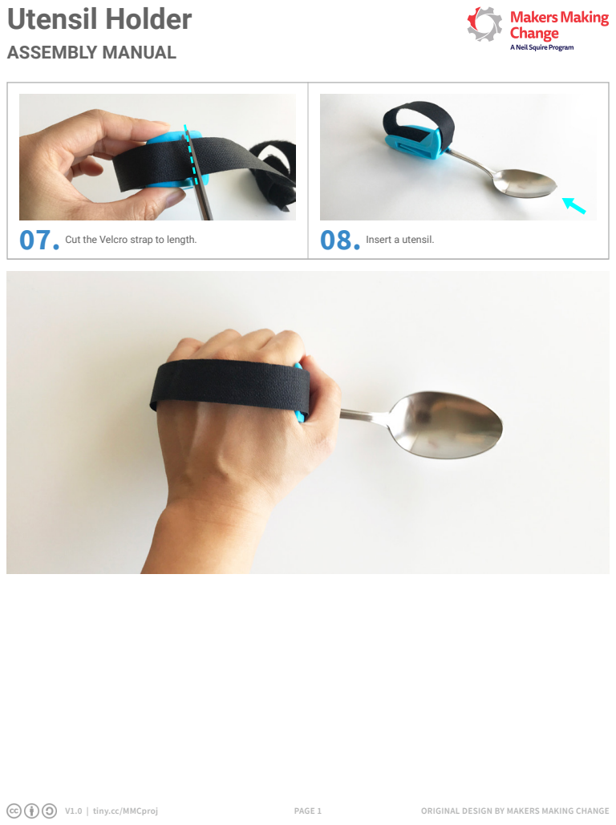
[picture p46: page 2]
V1.0 | tiny.cc/MMCproj; PAGE 1; ORIGINAL DESIGN BY MAKERS MAKING CHANGE; 07. Cut the Velcro strap to length.; 08. Insert a utensil.

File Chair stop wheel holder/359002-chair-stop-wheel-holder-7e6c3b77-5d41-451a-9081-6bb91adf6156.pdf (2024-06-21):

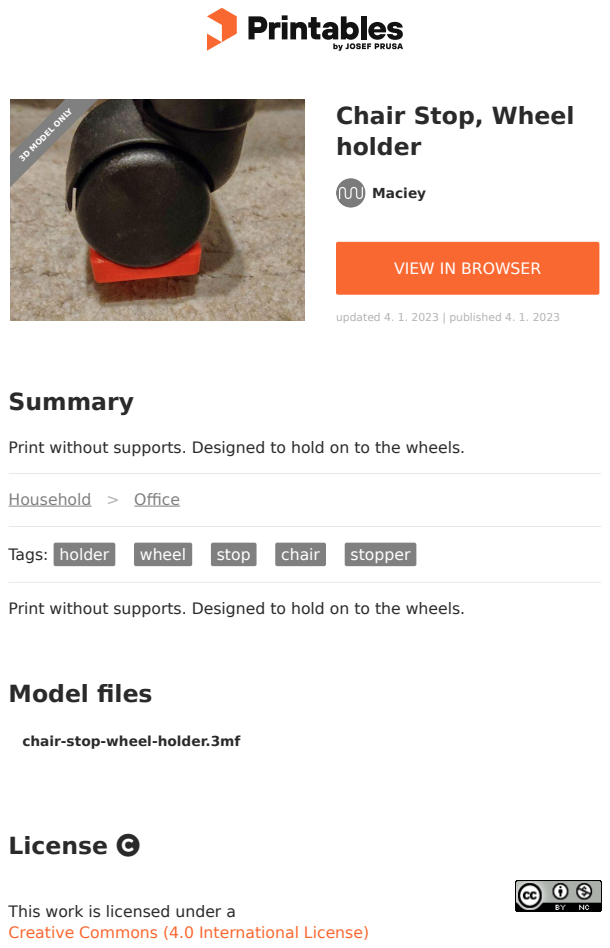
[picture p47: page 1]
Model files; Summary; Household > Office; Tags: holder; wheel; stop; chair; stopper; License; Maciey; updated 4. 1. 2023 | published 4. 1. 2023; 3D MODEL ONLY

Chair Stop, Wheel
holder

VIEW IN BROWSER (https://printables.com/model/359002-chair-stop-wheel-holder)

Print without supports. Designed to hold on to the wheels.

chair⁻stop-wheel-holder.3mf

This work is licensed under a
Creative Commons (4.0 International License) (http://creativecommons.org/licenses/by-nc/4.0/)

Attribution⁻NonCommercial (http://creativecommons.org/licenses/by-nc/4.0/)

✖ | Sharing without ATTRIBUTION
✔ | Remix Culture allowed
✖ | Commercial Use
✖ | Free Cultural Works
✖ | Meets Open Definition

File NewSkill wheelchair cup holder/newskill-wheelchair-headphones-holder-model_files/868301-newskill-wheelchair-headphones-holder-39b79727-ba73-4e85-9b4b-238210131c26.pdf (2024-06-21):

## NewSkill wheelchair

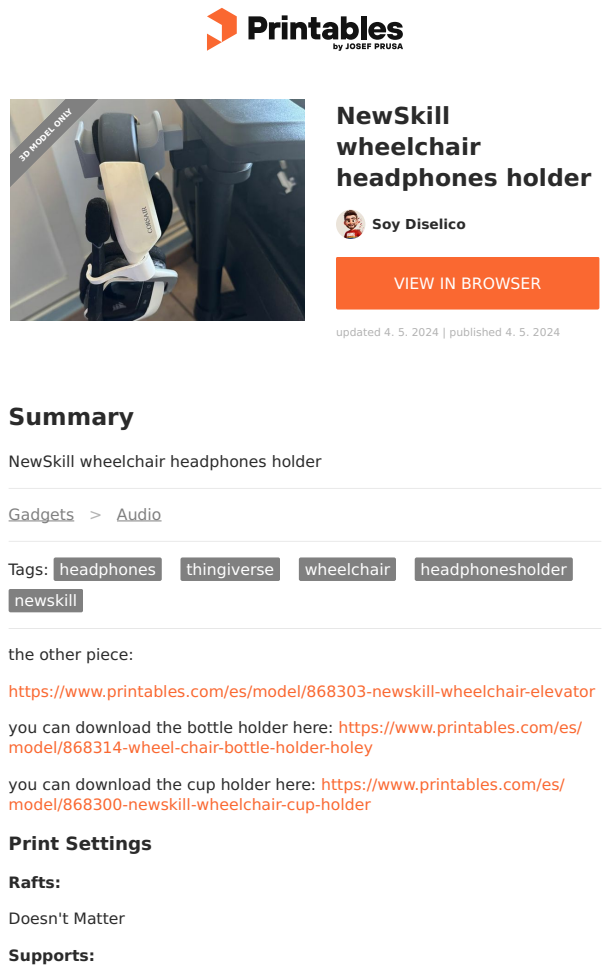
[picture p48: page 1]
Summary; Gadgets > Audio; Tags:; headphones; thingiverse; wheelchair; headphonesholder; newskill; Rafts:; Doesn't Matter; Supports:; Soy Diselico; headphones holder; updated 4. 5. 2024 | published 4. 5. 2024; 3D MODEL ONLY

VIEW IN BROWSER (https://printables.com/model/868301-newskill-wheelchair-headphones-holder)

NewSkill wheelchair headphones holder

the other piece:

https://www.printables.com/es/model/868303-newskill-wheelchair-elevator

you can download the bottle holder here: https://www.printables.com/es/
model/868314-wheel-chair-bottle-holder-holey (https://www.printables.com/es/model/868314-wheel-chair-bottle-holder-holey)

you can download the cup holder here: https://www.printables.com/es/
model/868300-newskill-wheelchair-cup-holder (https://www.printables.com/es/model/868300-newskill-wheelchair-cup-holder)
Print Settings

## Model files

Yes

Category: Audio

Find source .stl files on Thingiverse.com (https://www.thingiverse.com/thing:6606261)

## License

This work is licensed under a
Creative Commons (4.0 International License)

Attribution-ShareAlike (http://creativecommons.org/licenses/by-sa/4.0/)

✖ | Sharing without ATTRIBUTION
✔ | Remix Culture allowed
✔ | Commercial Use
✔ | Free Cultural Works
✔ | Meets Open Definition

headphones_holder.stl
